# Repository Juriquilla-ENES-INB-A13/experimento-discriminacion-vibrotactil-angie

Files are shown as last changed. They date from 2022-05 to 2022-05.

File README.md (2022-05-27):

This is the repo for Angie experiment. This include schematics and software also a manual about how to connect it

This project its made using the following software:
* Arduino IDE
* Processing 3.x
* Fritzing 0.9.x

# How to links
* Working with wire [(Sparkfun education site)](https://learn.sparkfun.com/tutorials/working-with-wire)
* How to crimp slim type harness [(Youtube video)](https://www.youtube.com/watch?v=8sHeR4Uozck)
* How to crimp molex type harness [(Youtube video)](https://www.youtube.com/watch?v=8jcfD1UW8SE) 

# Software

## Requirements
* Latest Processing 3.x from www.processing.org
* Install the following libraries using "Sketch -> Import libraries -> add libraries..."
	* G4P Controls library
	* G4P GUI Builder
	* Arduino library
	* Firmata library

## Instructions
1. Open processing.
2. Open project and point to software/manual_controller_2_vbr_last/manual_controller_2_vbr_last.pde
3. Select "file -> export application"
4. Select the current operating system.
5. Select "Embed java VM"
6. Click on "Export"
7. After completing, Processing will open a window with the executables (app for MacOS, sh for Linux, exe for windows).
8. Double click on the executable.

NOTE: The application stores all exported experiments in a text format under the "DATA" folder, everytime the application is recompiled this folder is deleted, so before compiling the application you should copy all the folder to another place to avoid loosing info.

# Hardware
## Tools
* 28-20 AWG Crimping pliers [Sparkfun site](https://www.sparkfun.com/products/13193) 
* 22-30 AWG Wire stripper [Sparkfun site](https://www.sparkfun.com/products/14762)
* Flush cutter [Sparkfun site](https://www.sparkfun.com/products/14782)
* Cutter
* Acrylic cutter
* 90° clamp holder
* Soldering iron
* Wire cutter

## Materials
* 20m 22 AWG Wire (Yellow, white, red,blue)
* [20 Dupont slim 4x1 connector](/images/dupont-slim4x1.jpeg)
* [100 Dupont slim female ferrule](/images/dupont-slim-female.jpg)
* [20 Female+male Molex 2510 3 pin with connectors](/images/molex-2510.jpg)
* Rosin flux
* RoHS Solder 0.7mm

## Electronics
* Latest Arduino from www.arduino.cc
	* Firmata library
* Arduino UNO Board
* Assembled Skinner Duino Shield  [get files](https://github.com/Juriquilla-ENES-INB-A13/SkinnerDuino-shield)
* Assembled Power Servo PCB (under circuits folder)

### Sensors Connection

#### SkinerDuino shield
* SkinnerDuino has a set of pins for sensors, and they are labeled as DIO, the wiring is as follows:
	* 5V GND 8
	* 5V GND 7
	* 5V GND 4
	* 5V GND 2

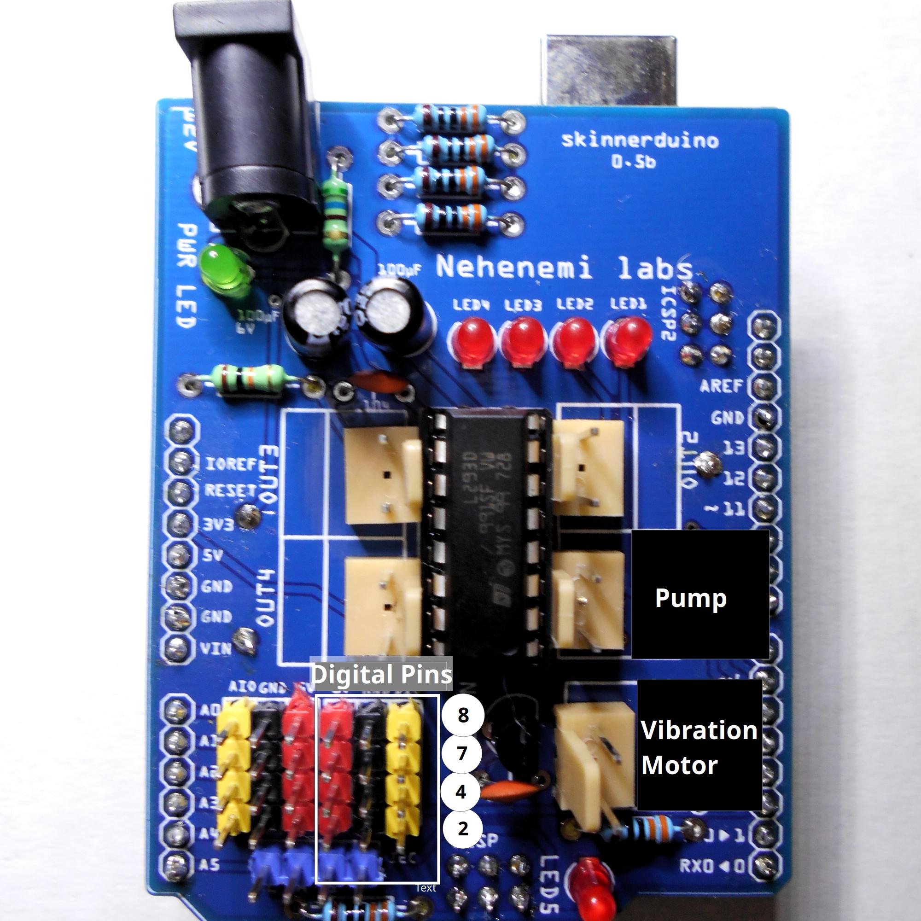
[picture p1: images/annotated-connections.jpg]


	This pins are connected to the same numbered digital pins in Arduino UNO.

* Other Connections
	* Vibration motor connected to OUT3.3V
	* Left pump connected to OUT1
	* Right pump connected to OUT2

* Power
	* The peristaltic pumps need between 24V to 26V so you need a power source with 5mm barrel connector.
	* For avoiding issues, dont add or desolder ALL electrolitic capacitors, and the green LED.

#### Poke and Inside Sensor
* FC-51 Obstacle distance IR sensor
* Connector from top
	OUT GND VCC

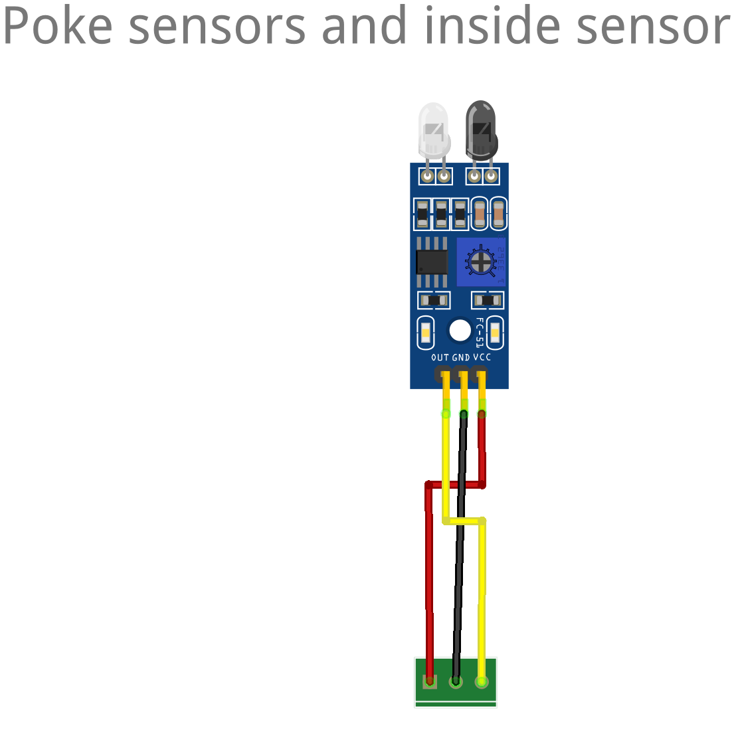
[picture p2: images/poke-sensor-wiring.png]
	

#### Peristaltic pump
* Campden Instruments 80204A pump
	* 24V - 28V
	* Connections
		* RED Power
		* Blue Operate
		* Green 0V/GND

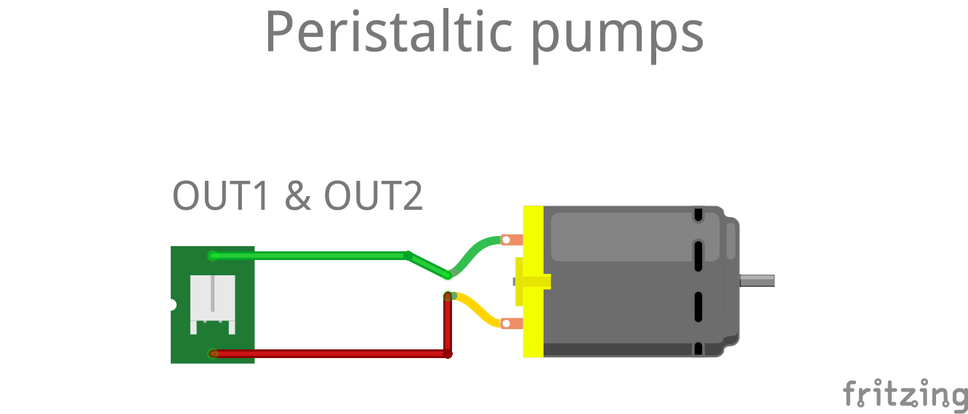
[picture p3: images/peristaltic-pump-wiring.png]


#### Skinner Duino Connections
|Item                |  Port  |
|--------------------|--------|
|Vibration motor     |OUT 3.3V|
|Pump                | OUT 1  |
|Poke sensor left    |   8    |
|Poke sensor right   |   7    |
|Servo door          |   4    |
|Internal IR Sensor  |   2    |

# Software

## Instructions
The software needs a firmware called firmata, which has to be uploaded to the Arduino UNO Board

### Arduino
1. Open Arduino IDE
2. Install Firmata library
3. Open menu "Examples -> firmata -> Standard firmata"
4. Select on which port is the Arduino UNO board connected.
5. Check on menu "Tools -> Board" that "Arduino UNO" board is selected.
6. Upload the firmware to the board.

### Processing

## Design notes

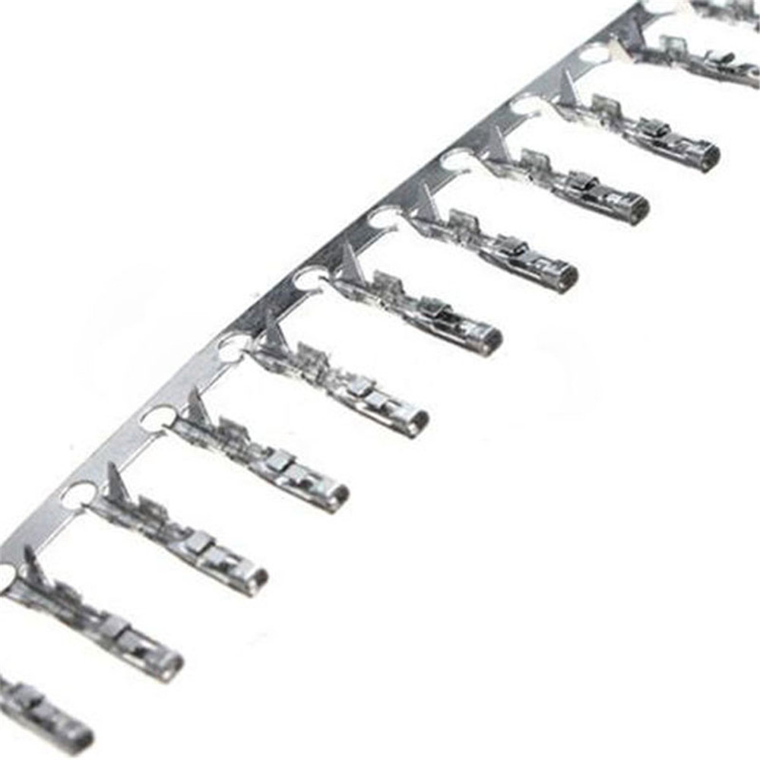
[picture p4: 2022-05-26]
images/dupont-slim-female.jpg

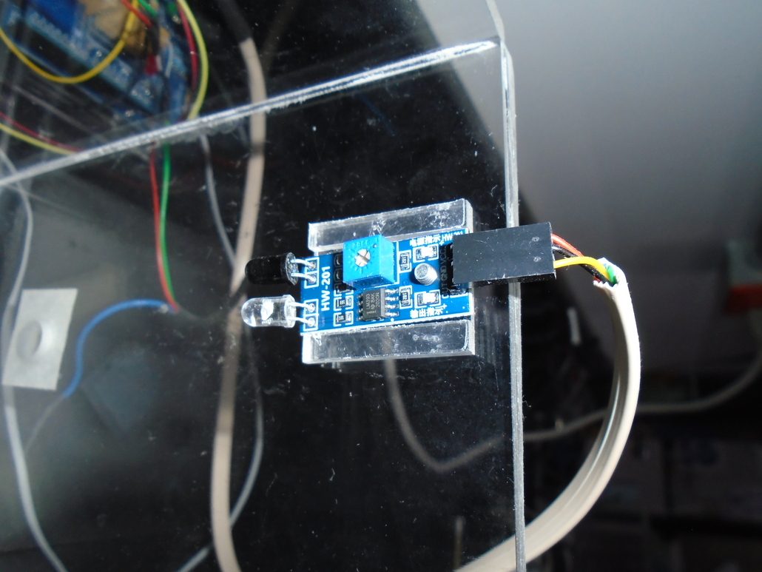
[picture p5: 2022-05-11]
images/in-sensor.JPG

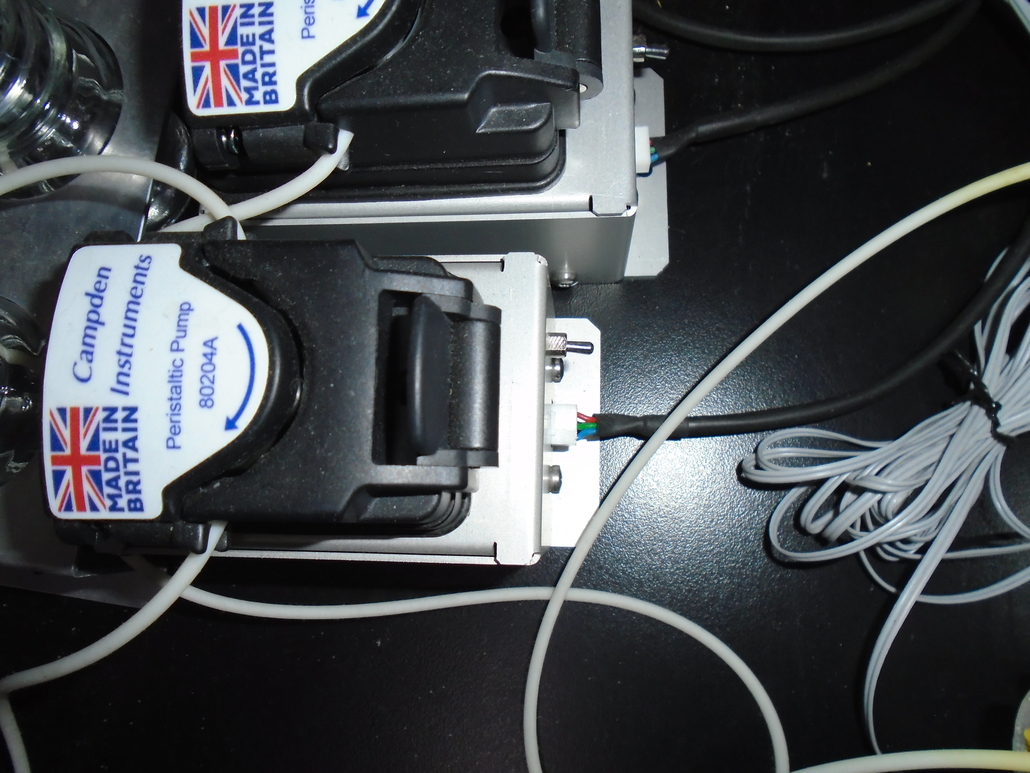
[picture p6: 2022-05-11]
images/peristaltic-pump.JPG

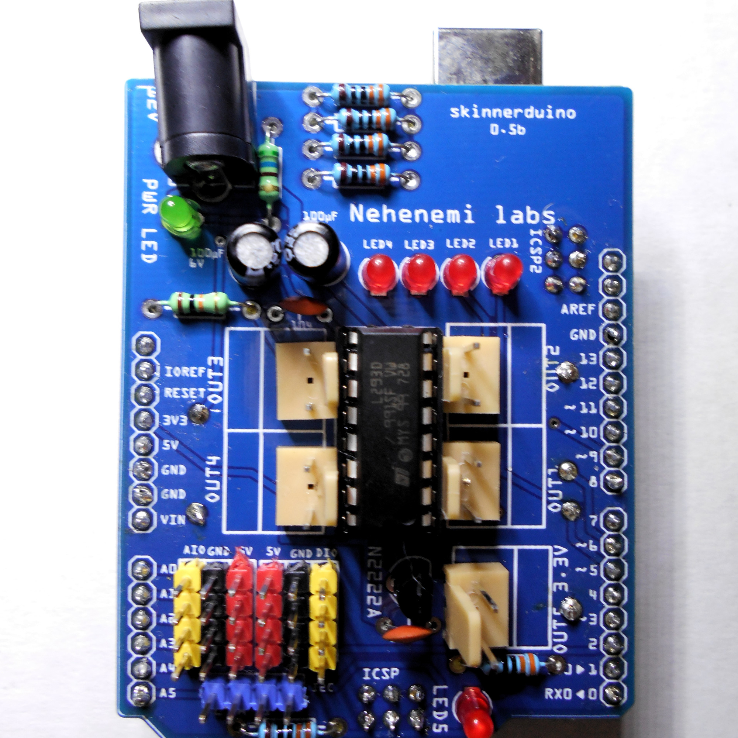
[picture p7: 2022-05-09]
images/pcb-0-5b.JPG

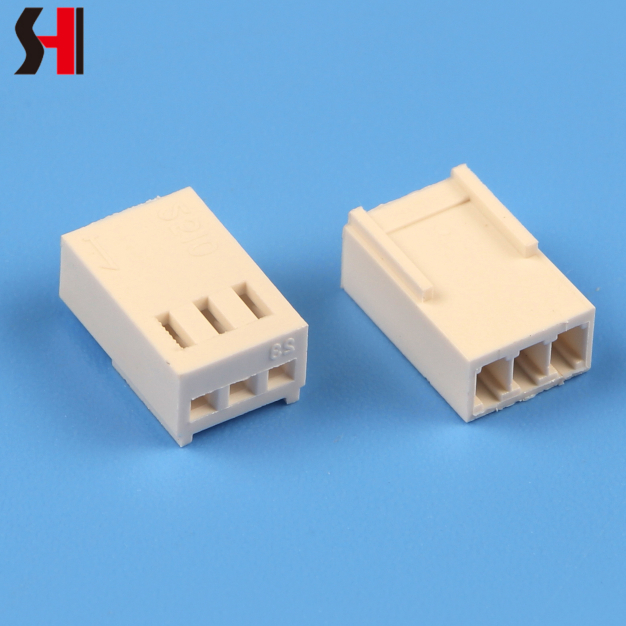
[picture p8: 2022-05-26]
images/molex-2510.jpg

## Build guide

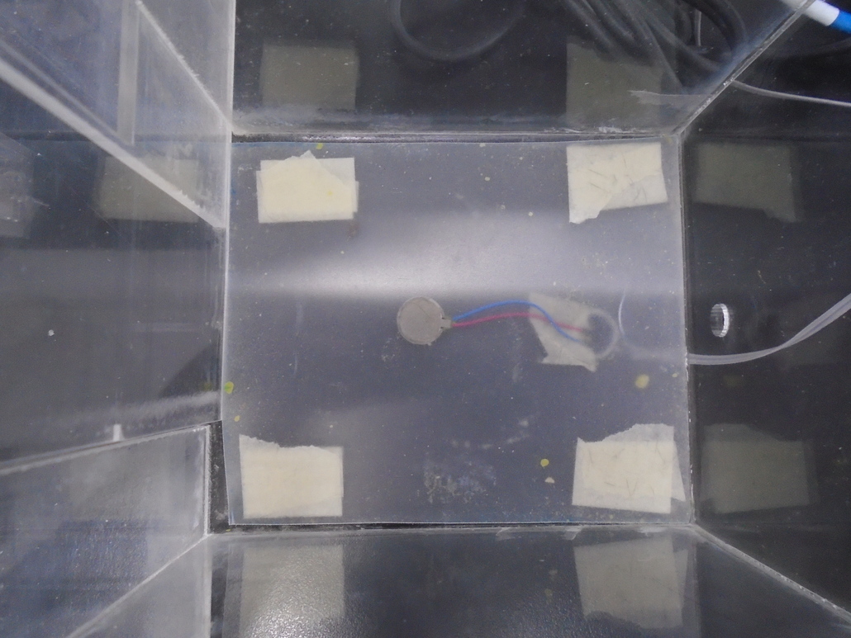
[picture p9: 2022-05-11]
images/vibration-motor-assembly.JPG

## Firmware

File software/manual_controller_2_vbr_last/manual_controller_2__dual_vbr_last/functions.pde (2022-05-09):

//common functions
void setArduino(){
  if(ardu != null){
    ardu.dispose();
    println("INFO:arduino disconnected!");
  }
  println("INFO:connecting to port:"+Arduino.list()[lst_port.getSelectedIndex()]);
  ardu = new Arduino(this, Arduino.list()[lst_port.getSelectedIndex()], 57600);
  ardu.pinMode(vibr, Arduino.OUTPUT);
  ardu.pinMode(pumpL, Arduino.OUTPUT);
  ardu.pinMode(pumpR, Arduino.OUTPUT);
  ardu.pinMode(pokeL, Arduino.INPUT);
  ardu.pinMode(pokeR, Arduino.INPUT);
  ardu.pinMode(door, Arduino.SERVO);
  ardu.pinMode(inSensor, Arduino.INPUT);
  ardu.pinMode(10,Arduino.OUTPUT);
  ardu.servoWrite(door,closeAngle);
  doorOpen=false;
  //This make arduino signal an ok connection
  delay(1000);
  ardu.digitalWrite(10,Arduino.HIGH);
  delay(100);
  ardu.digitalWrite(10,Arduino.LOW);
  delay(100);
  ardu.digitalWrite(10,Arduino.HIGH);
  delay(100);
  ardu.digitalWrite(10,Arduino.LOW);
  println("INFO:success!");
  lbl_connected.setText("connected!");
  btnCloseDoor.setVisible(true);
  btnOpenDoor.setVisible(true);
  btnVibrateHigh.setVisible(true);
  btnVibrationLow.setVisible(true);
  btn_start.setVisible(true);
  btn_feedL.setVisible(true);
  btn_fillL.setVisible(true);
  btnFeedR.setVisible(true);
  btnFillR.setVisible(true);
  
}

void appendTextToFile(String filename, String text) {
  File f = new File(dataPath(filename));
  if (!f.exists()) {
    createFile(f);
  }
  try {
    PrintWriter out = new PrintWriter(new BufferedWriter(new FileWriter(f, true)));
    out.println(text);
    out.close();
  }
  catch (IOException e) {
    e.printStackTrace();
  }
}

void createFile(File f) {
  File parentDir = f.getParentFile();
  try {
    parentDir.mkdirs(); 
    f.createNewFile();
  }
  catch(Exception e) {
    e.printStackTrace();
  }
}

//Motor functions
void fillL()
{
  println("RUN:Filling!");
  ardu.analogWrite(pumpL, 255);
  delay(3000);
  ardu.analogWrite(pumpL, 0);
  println("RUN:Done!");
}
void fillR() //<>//
{
  println("RUN:Filling!");
  ardu.analogWrite(pumpR, 255);
  delay(3000);
  ardu.analogWrite(pumpR, 0);
  println("RUN:Done!");
}

void feedL()
{
  println("RUN: feedL");
  int power;
  if(sldPower.getValueF()>0){
    power=int(sldPower.getValueF()*2.55);
  }else{
    power=0;
  }
  ardu.analogWrite(pumpL,power);
  delay(fld_pump_pulse.getValueI());
  ardu.analogWrite(pumpL, 0);
  delay(50);
  if(runExperiment){
    appendTextToFile(filename,iteration+","+(millis()-timeStart)+",feedL");
    feedTimesL++;
  }
}

void feedR()
{
  println("RUN: feedR");
  int power;
  if(sldPower.getValueF()>0){
    power=int(sldPower.getValueF()*2.55);
  }else{
    power=0;
  }
  ardu.analogWrite(pumpR,power);
  delay(fld_pump_pulse.getValueI());
  ardu.analogWrite(pumpR, 0);
  delay(50);
  if(runExperiment){
    appendTextToFile(filename,iteration+","+(millis()-timeStart)+",feedR");
    feedTimesR++;
  }
}

void openDataFolder() {
  println("Opening folder:"+dataPath(""));
  if (System.getProperty("os.name").toLowerCase().contains("windows")) {
    launch("explorer.exe"+" "+dataPath(""));
  } else {
    launch(dataPath(""));
  }
}

void writeTableHeader(String flname)
{
  appendTextToFile(flname, "repeat,freq,poke_time,touched_poke,inside_time,status");
}

void writeSeparator(String flname)
{
  appendTextToFile(flname, "");
}

void closeDoor(){
  if(!doorOpen){
    println("Door already closed");
    return;
  }
  ardu.pinMode(door,Arduino.SERVO);
  while(door_angle>closeAngle){
    ardu.servoWrite(door,door_angle);
    door_angle--;
    println(door_angle);
    delay(doorDelay);
  }
  doorOpen=false;
}

void openDoor(){
  if(doorOpen){
    println("Door already open");
    return;
  }
  door_angle = openAngle;
  ardu.pinMode(door,Arduino.SERVO);
  for(door_angle=closeAngle;door_angle<openAngle;door_angle++){
    ardu.servoWrite(door,door_angle);
    println(door_angle);
    delay(doorDelay);
  }
  doorOpen=true;
}

void addWindowInfo(){
  surface.setTitle("Dual Manual Stage "+day()+"-"+month()+"-"+year()+" "+hour()+":"+minute()+":"+second()+ "  Iteration:"+iteration+ " OK:"+numOk+" Fail:"+numFail);
}


//Experiment specific functions

boolean checkFields() {

  if ((fldVibrDur.getValueI() != 0) || 
  (fld_name.getText() != "")) {
    return true;
  } else {
    println("ERROR: No empty fields allowed! ");
    return false;
  }
}

void writeParamsToFile(String flname)
{
  println("FILE: "+flname);
  String datetime = new String(day()+"-"+month()+"-"+year()+" "+hour()+":"+minute()+":"+second());
  println(datetime);
  String params = new String(
   

  );
  println(params);
  appendTextToFile(flname, "started: "+datetime);
  appendTextToFile(flname, params);
}

void stopExperiment(){
  runLoop=false;
  runExperiment=false;
}

void randomizeFreq()
{
  if(int(random(2))==1){
    freq=20;
  }else{
    freq=40;
  }
}

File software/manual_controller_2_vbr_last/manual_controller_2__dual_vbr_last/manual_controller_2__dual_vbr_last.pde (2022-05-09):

/*
Manual control for double pumps
*/


import g4p_controls.*;
import java.io.BufferedWriter;
import java.io.FileWriter;
import java.lang.*;
import cc.arduino.*;
import org.firmata.*;
import processing.serial.*;

//connections
int vibr = 3;
int pumpL = 5;
int pumpR = 6;
int pokeL = 8;
int pokeR = 7;
int door = 4;
int inSensor = 2;

boolean doorOpen;
boolean runLoop;
boolean runExperiment=false;
boolean abortExperiment=false;
int sensingInsideTime;
int port = 0;
int timeFeed = 5;
int cycleFeed = 10;
int closeAngle = 10;
int openAngle = 52;
int doorDelay = 12;
int numOk = 0;
int numFail = 0;
int numIteration = 0;
int freq;
int vibr_dur;
int door_time;
int timeStart;
int timeStop;
int door_angle;
int waitForNextExperiment;
int repeats;
int pokeTime;
int insideTime;
int InR;
int InL;
int InW;
int insideWait;
int timesFeed;
int iteration;
int maxFreq = 80;
int minFreq = 20;
int feedTimesL=0;
int feedTimesR=0;
String filename;
boolean feedIt;
boolean touchedPoke;
boolean feeding=false;
boolean waitingPoke=false;
String whichPoke="none";
String status="null";


//objects
Arduino ardu;

public void setup(){
  size(630, 410, JAVA2D);
  println(Arduino.list());
  createGUI();
  customGUI();
}

public void draw(){
  background(230);
}

// Use this method to add additional statements
// to customise the GUI controls
public void customGUI(){
  


 fld_feed_r.setNumericType(G4P.INTEGER);
 fld_feed_l.setNumericType(G4P.INTEGER);
 fld_wait_to_feed.setNumericType(G4P.INTEGER);
 fld_wait_to_feed.setText("0");
 fld_pump_pulse.setNumericType(G4P.INTEGER);
 fld_pump_pulse.setText(Integer.toString(timeFeed));

 fldVibrDur.setNumericType(G4P.INTEGER);
 fldVibrDur.setText("1000");
 btn_stop.setVisible(false);
   btnCloseDoor.setVisible(false);
  btnOpenDoor.setVisible(false);
  btnVibrateHigh.setVisible(false);
  btnVibrationLow.setVisible(false);
  btn_start.setVisible(false);
  btn_feedL.setVisible(false);
  btn_fillL.setVisible(false);
  btnFeedR.setVisible(false);
  btnFillR.setVisible(false);
}

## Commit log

2022-05-26 Added materials
2022-05-27 Added PCB for servo power
    [Power Servo PCB.fzz, Power Servo PCB_contour.gm1, Power Servo PCB_copperBottom.gbl, Power Servo PCB_copperTop.gtl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]
